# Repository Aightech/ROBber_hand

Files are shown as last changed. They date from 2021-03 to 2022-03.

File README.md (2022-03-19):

# Robotics ROBber Hand

## Description
ROBber hand is a robotic version of the rubber hand experiment. A webcam captures the position of the fingertips (with colour markers) and sends the angle to the device. The device is composed of four servo motors driven by a PCA9685 driver and an Arduino Uno. A fake hand is placed on top of the device and each finger is pushed up by the device.

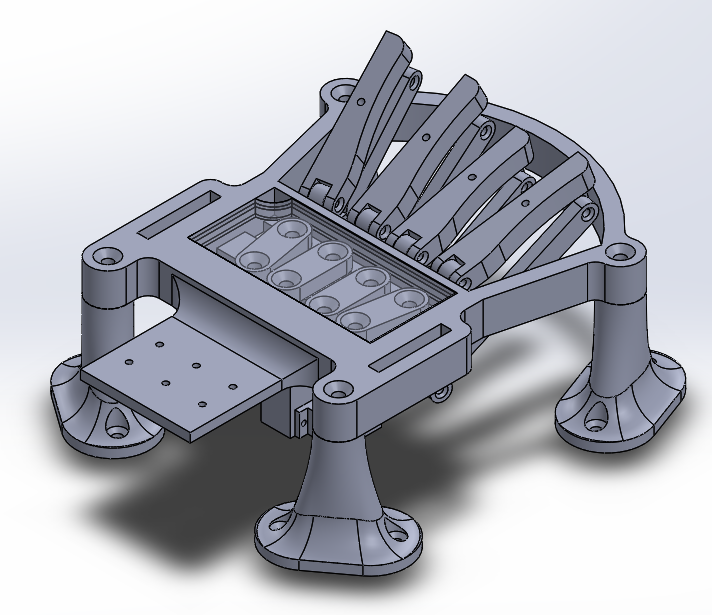
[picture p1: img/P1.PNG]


### List of material
- 4 servos motors MG90(metal gear) or SG90 (plastic gears)
- 1 servo driver PCA9685
- 1 arduino
- Screws and Bolts:
  - 8 M3-12mm
  - 4 M3-16mm
  - 12 M5-20mm
  - 4 M5 bolt

### Parts to print
- 1 frame
- 1 lid
- 4 foot
- 1 arduinoUNO and PCA holder
- 2 p1_short
- 2 p1_long
- 4 p2
- 2 p3_short
- 2 p3_long
- 2 p4_short
- 2 p4_long
- 4 bolt

## Requirements
- Python3/pip installed.

## Installation
### Electronics
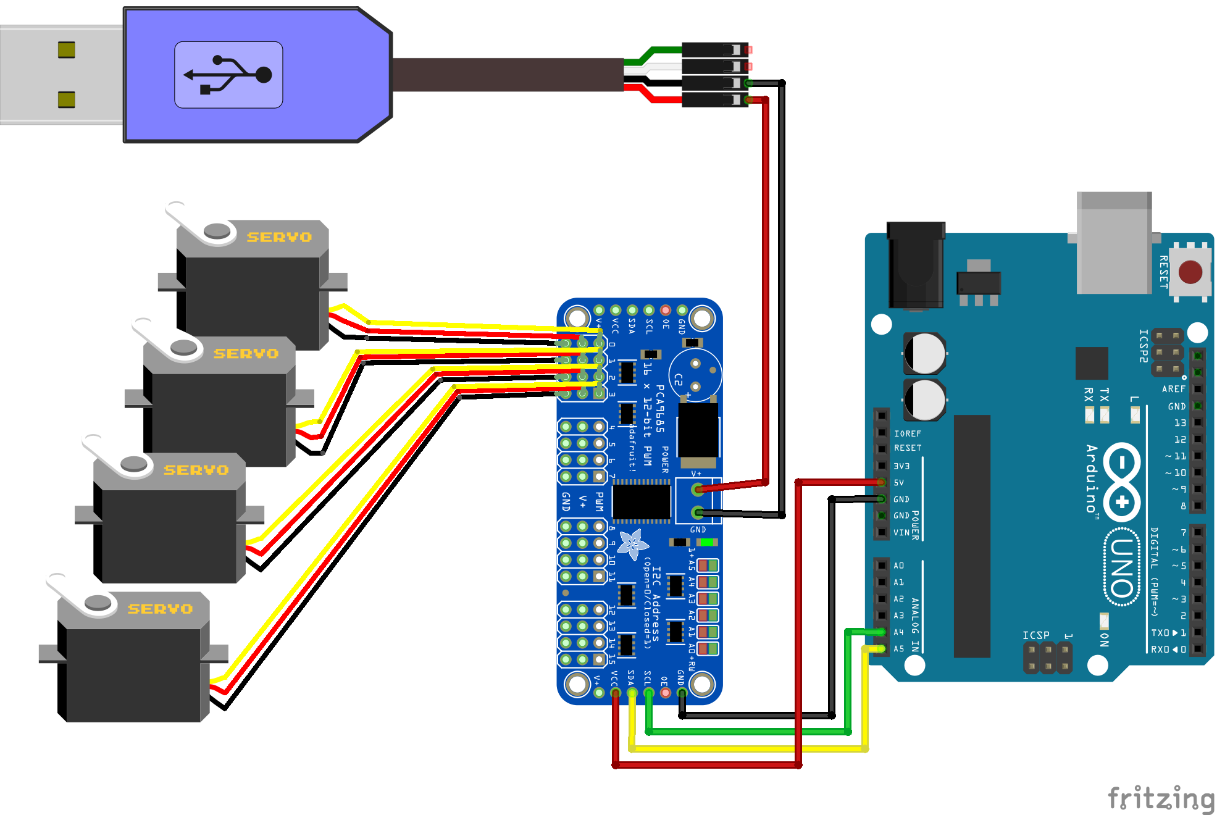
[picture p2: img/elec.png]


### Firmware
- Plug the arduino to the computer.
- Open the arduino IDE
- Ensure you have the last verdion of the library **Adafruit PWM Servo Driver** (go to the menu _sketch>Include library>Libraries Manager_ and search for "PWM".
- Open the file scripts/arduino.ide of the repository
- Upload it on the arduino board. 

### Software
- Download the zip folder at https://github.com/Aightech/ROBber_hand .
- Extract it
- Open the folder.
- Open the folder named **scripts**
- While pressing the **shift key** right click in the folder and select the option **open PowerShell**

Inside the PowerShell terminal:
- Install required libraries by entering the following command in the PowerShell terminal.
```bash 
pip install -r requirements.txt
```
## Usage

### Setup
- Plug the arduino USB wire to the computer.
- Plug the Webcam to the computer.
- Connect the motor driver to a power supply (ex: a phone charger).

### Setting:
To ensure the different parameters of the experiments are correct run the program setting with the command:
```bash 
python setting.py <NB_CAM> 
```
Replace :
- **<NB_CAM>** by the number of the webcam (usually 1 for laptop with integrated cam, else 0).

### Experiment
To launch the experiment use the command:
```bash 
python run.py <ARDUINO_PORT> <NB_CAM>
```
Replace :
- **<ARDUINO_PORT>** by the port used by the arduino (usually COM3, COM4, ...).
- **<NB_CAM>** by the number of the webcam (usually 1 for laptop with integrated cam, else 0).

### Options

in the script named **scripts/run.py** you can modify the following lines to modify the behavior of the robot.
```python
# BUFFER SIZE AND LOOKUP TABLE
lookup_table = [0, 1, 2, 3] # [nb finger cmd] => nb finger controlled
BUFF_SIZE = 1 # Delay of the control (no unit... depends of you communication speed)
inverted_finger = False  # When human finger up => robot finger down 
```

# Debug

In a terminal you can use the script **sendCmd.sh** to send position order to the Robber hand. Here an exemple:
```bash
Usage: scripts/sendCmd.sh [pos1] [pos2] [pos3] [pos4] port
Ex: scripts/sendCmd.sh 20 40 50 60 /dev/ttyUSB0
```

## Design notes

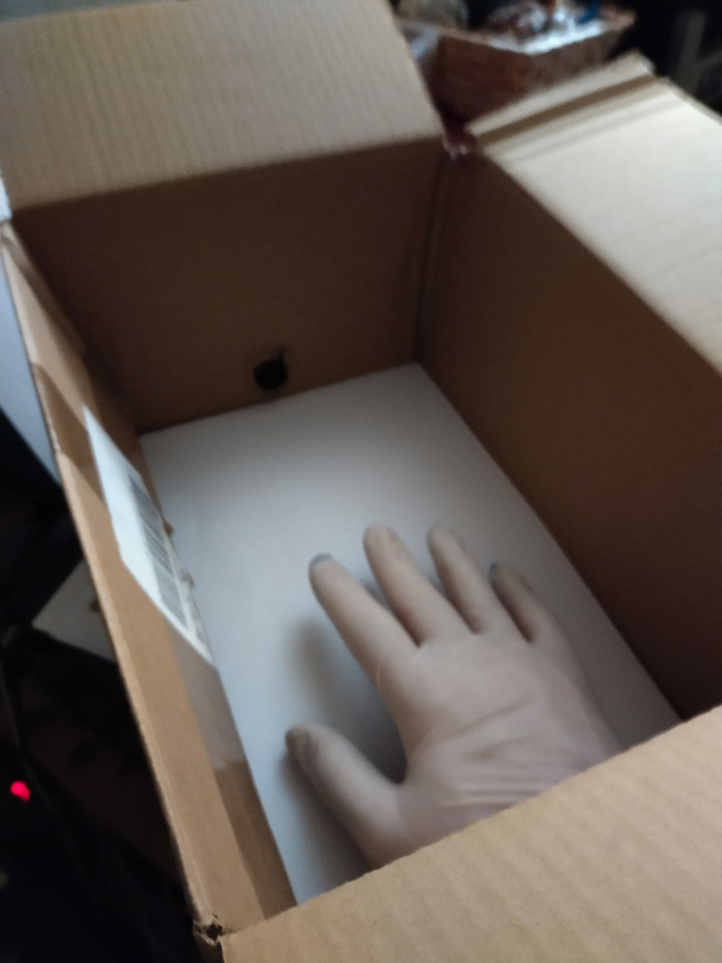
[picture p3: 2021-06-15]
img/SAVE_20210615_120732.jpg

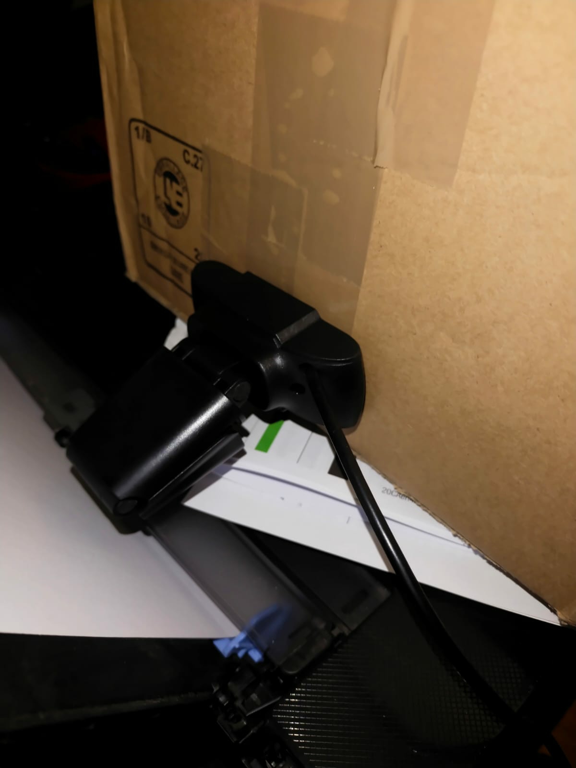
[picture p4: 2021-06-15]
img/SAVE_20210615_120804.jpg

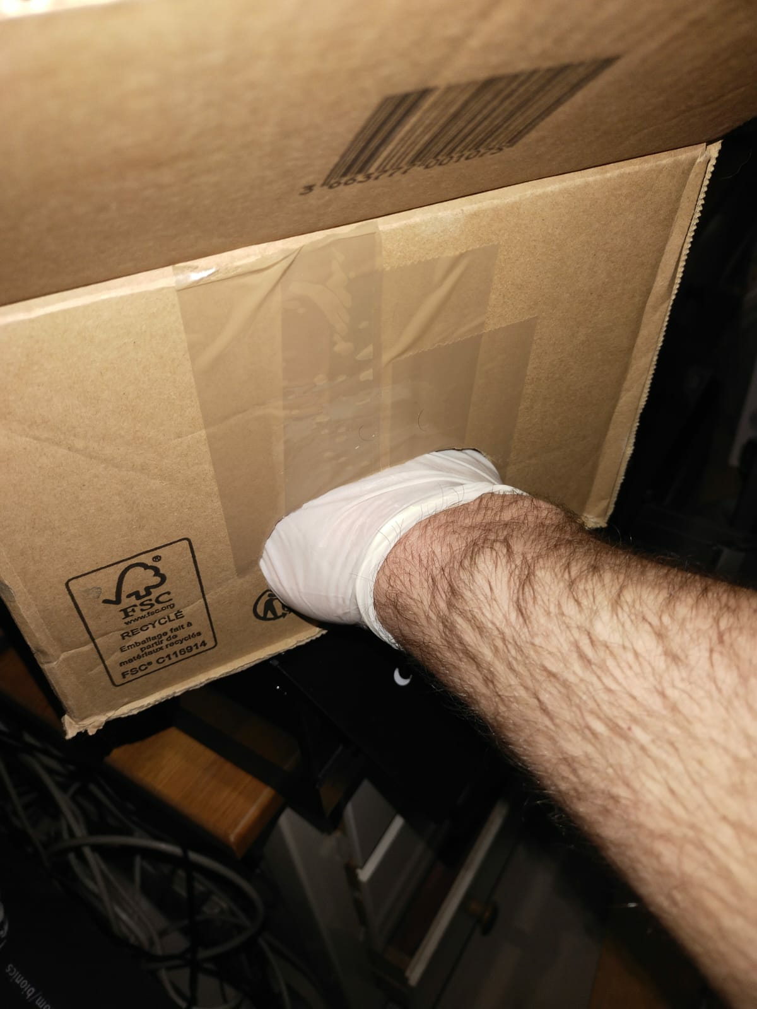
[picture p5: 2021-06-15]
img/SAVE_20210615_120755.jpg

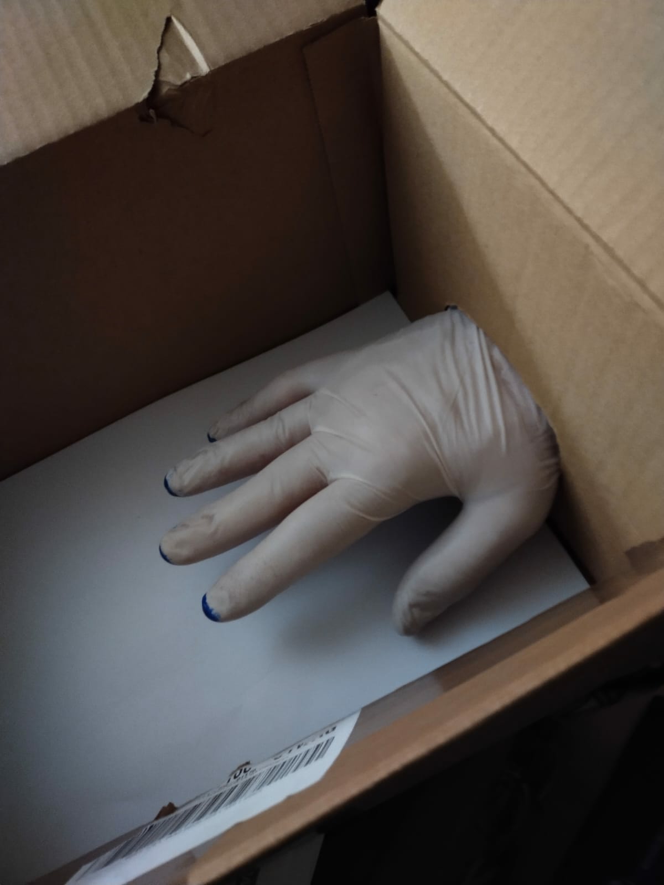
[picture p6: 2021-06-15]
img/SAVE_20210615_120743.jpg

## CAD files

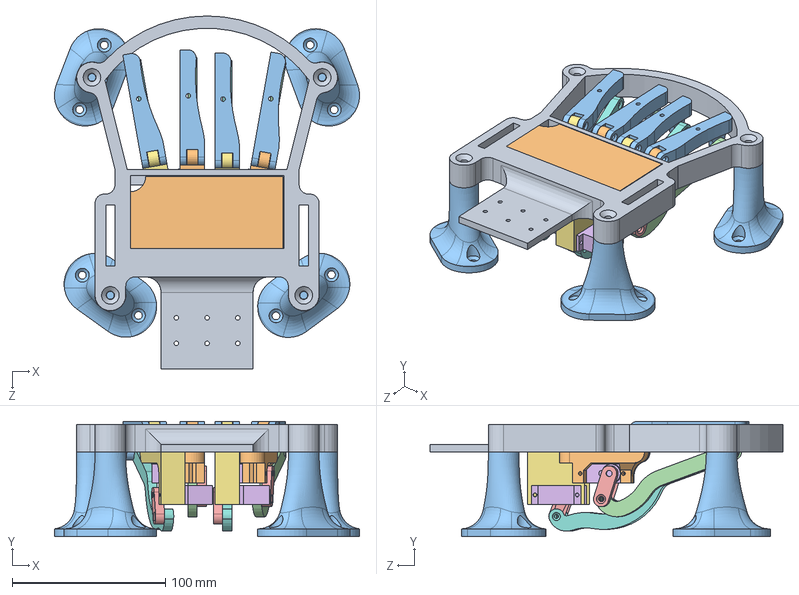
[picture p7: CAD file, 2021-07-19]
models/assemblage.SLDASM
198.7 x 75.0 x 230.0 mm
frame
p1_short x 2
p2 x 4
p3_short x 2
p4 x 4
sg90 x 4
p1_long x 2
p3_long x 2
bolt x 4
lid
foot x 4

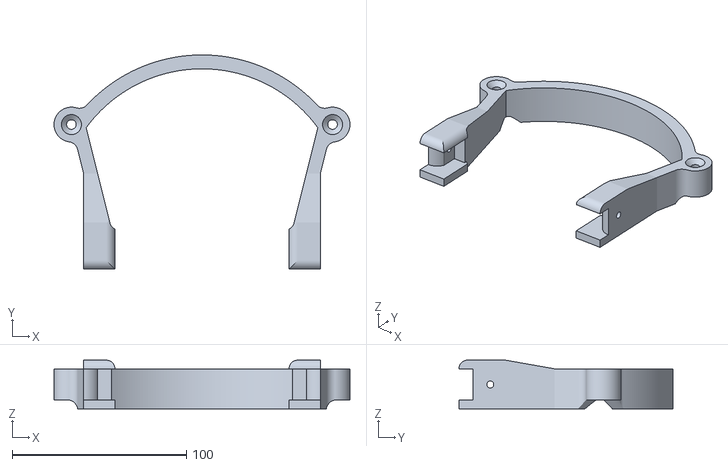
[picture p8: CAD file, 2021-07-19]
models/frame_v2-top.STL
170.0 x 123.0 x 28.0

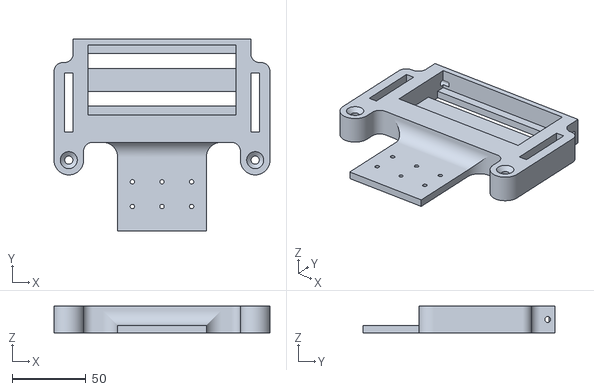
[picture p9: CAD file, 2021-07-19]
models/frame_v2-bottom.STL
146.0 x 130.0 x 18.0

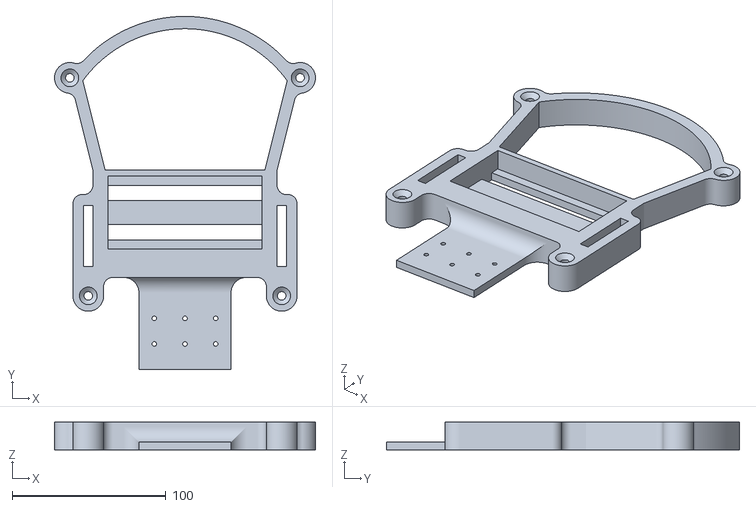
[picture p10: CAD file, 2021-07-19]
models/frame_Défaut.STL
170.0 x 230.0 x 18.0

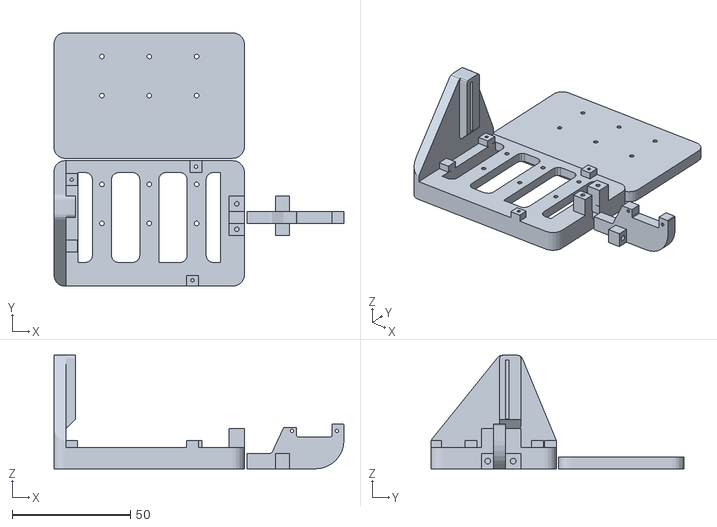
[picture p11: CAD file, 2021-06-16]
models/arduinoUNO_PCA_holder.stl
122.5 x 107.0 x 48.0

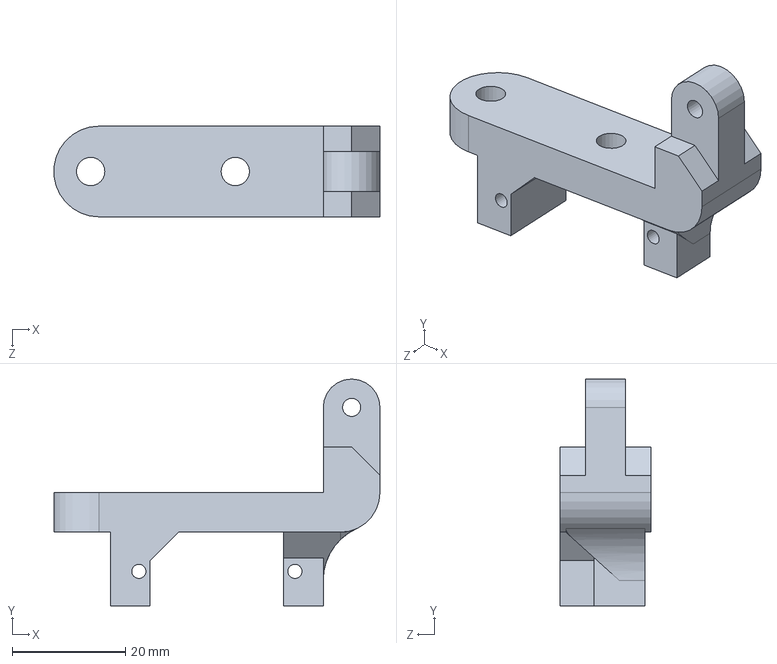
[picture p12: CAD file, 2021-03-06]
models/p1_short.SLDPRT
57.5 x 40.0 x 16.0 mm

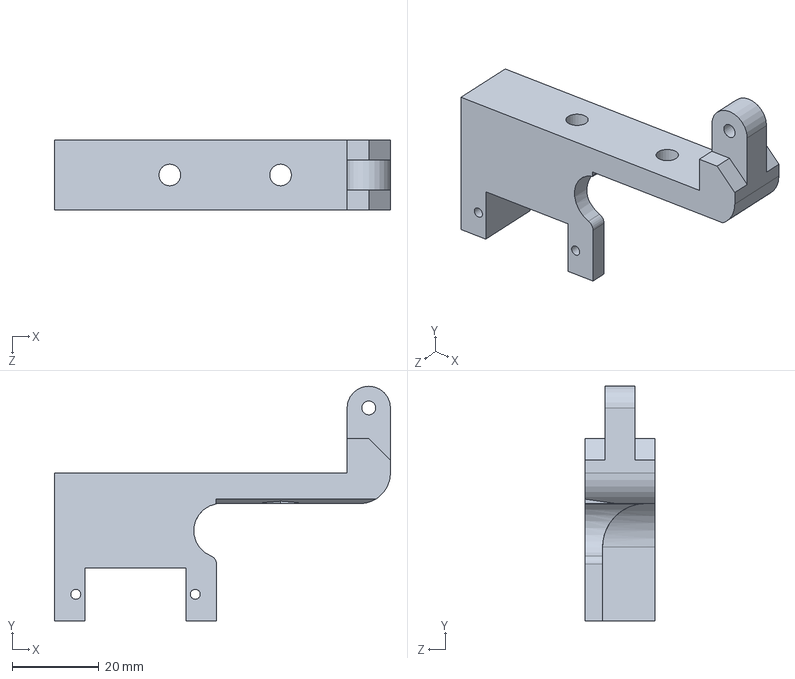
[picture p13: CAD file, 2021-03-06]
models/p1_long.SLDPRT
77.3 x 54.0 x 16.0 mm

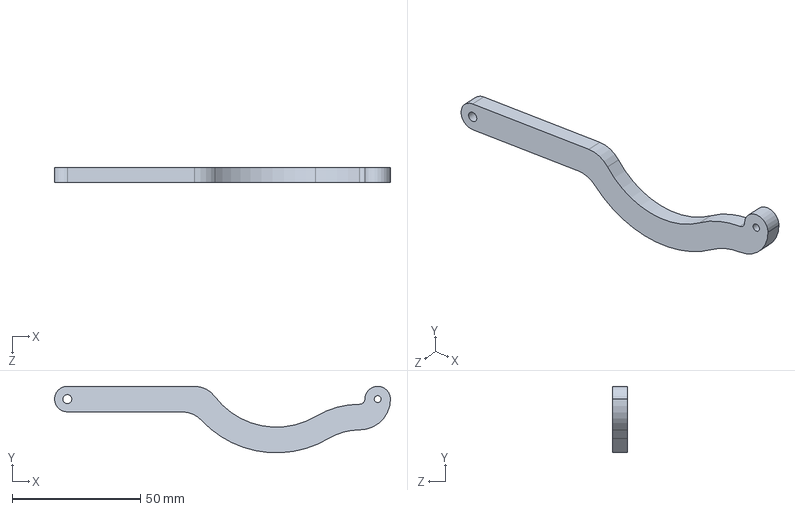
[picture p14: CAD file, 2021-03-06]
models/p3_long.SLDPRT
131.0 x 25.9 x 6.00 mm

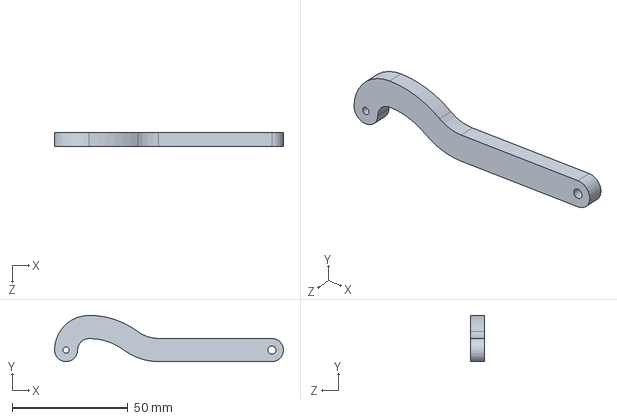
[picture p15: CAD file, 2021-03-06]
models/p3_short.SLDPRT
99.0 x 20.0 x 6.00 mm

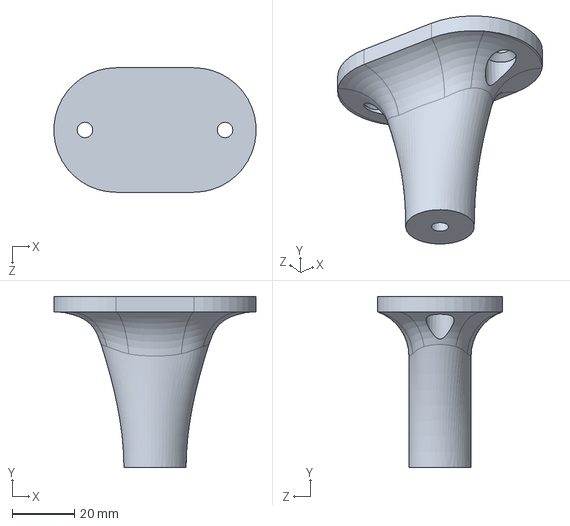
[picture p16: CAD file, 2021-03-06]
models/foot.SLDPRT
64.9 x 55.0 x 40.0 mm

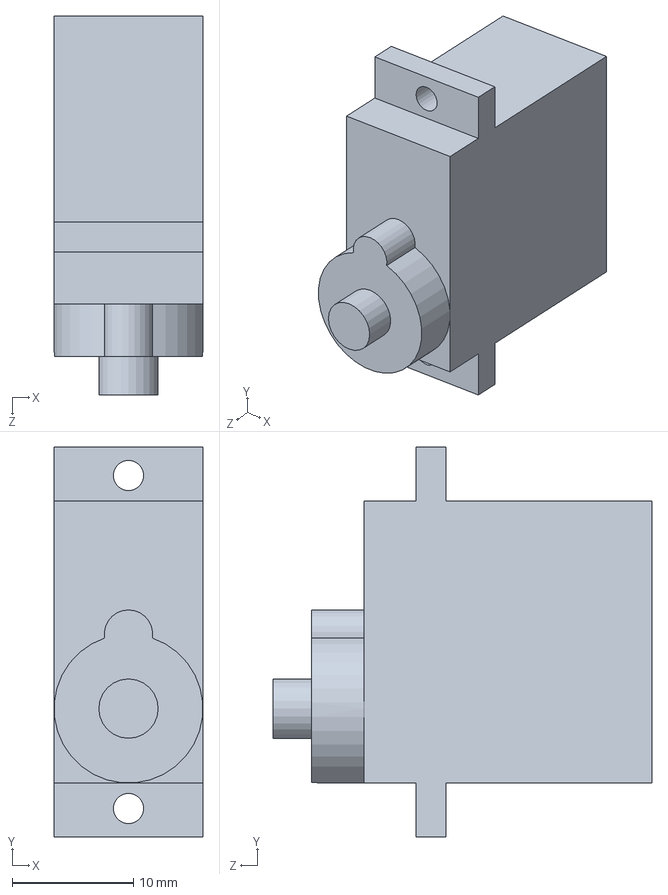
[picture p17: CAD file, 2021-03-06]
models/sg90.SLDPRT
12.3 x 32.2 x 31.3 mm

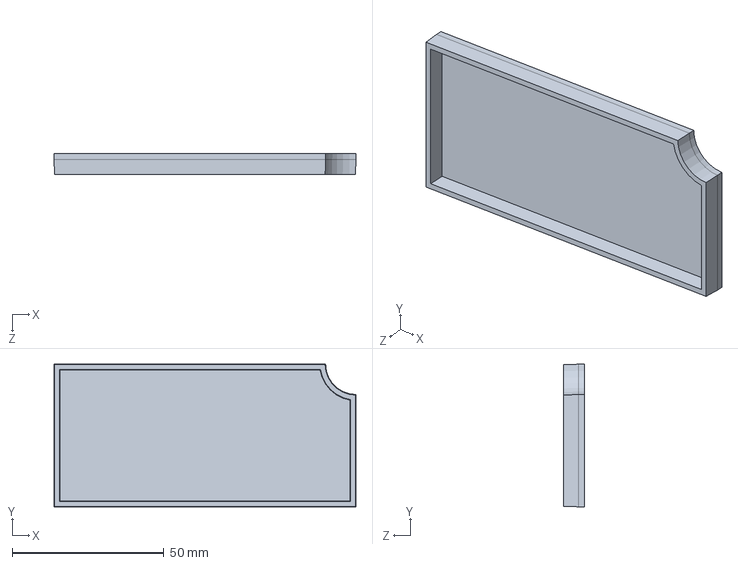
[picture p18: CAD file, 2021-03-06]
models/lid.SLDPRT
99.5 x 47.0 x 7.00 mm

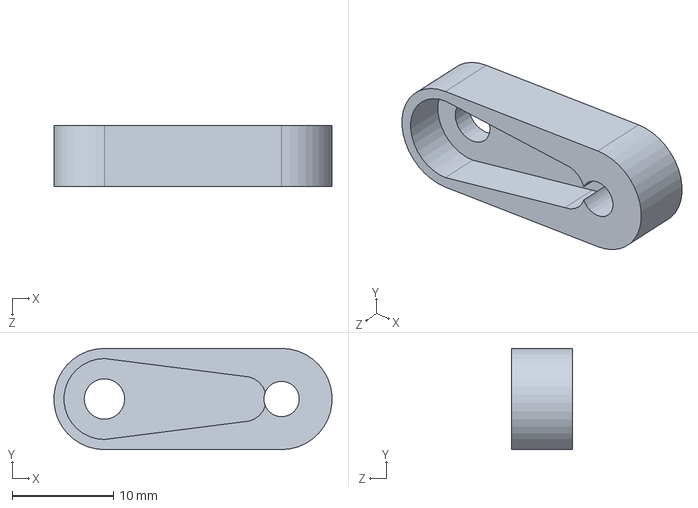
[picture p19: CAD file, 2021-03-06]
models/p4.SLDPRT
27.5 x 10.0 x 6.00 mm

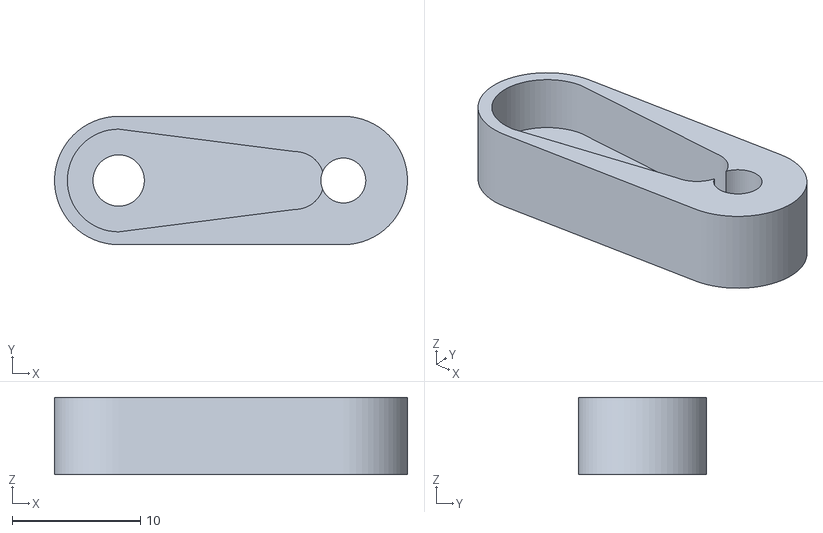
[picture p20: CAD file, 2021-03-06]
models/p4_short.STL
27.5 x 10.0 x 6.00

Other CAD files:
models/frame.SLDPRT
models/p4_long.STL
models/p2.SLDPRT
models/bolt.SLDPRT
models/assemblage.STL
models/bolt.STL
models/foot.STL
models/frame.STL
models/lid.STL
models/p1_long.STL
models/p1_short.STL
models/p2.STL
models/p3_long.STL
models/p3_short.STL

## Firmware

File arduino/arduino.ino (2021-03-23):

#include <Wire.h>
#include <Adafruit_PWMServoDriver.h>

Adafruit_PWMServoDriver pwm = Adafruit_PWMServoDriver();

//#define DEBUG
#define NB_FINGER 4
#define SERVOMIN  440 // This is the 'minimum' pulse length count (out of 4096)
#define SERVOMAX  470 // This is the 'maximum' pulse length count (out of 4096)
int s_range = SERVOMAX-SERVOMIN;

unsigned char crc;
unsigned char pos[NB_FINGER] = {20, 00, 100, 00};
int limit[NB_FINGER][2] = { {400, 280},
                                      {200, 385},
                                      {320, 170},
                                      {180, 360}};

void setup() {
  Serial.begin(9600);
  pinMode(13, OUTPUT);

  pwm.begin();
  pwm.setOscillatorFrequency(27000000);
  pwm.setPWMFreq(50);  // This is the maximum PWM frequency

   
}

void loop() {

 #ifdef DEBUG
//    for(int i =0; i<NB_FINGER; i++)
//         pwm.setPWM(i, 0, pos[i]/255.0f*(limit[i][1]-limit[i][0])+limit[i][0]);
    delay(15);
    int i = 3;
    pwm.setPWM(i, 0, 200);
  #endif
   
  
  while (Serial.available() > NB_FINGER+3)//wait for data
  {
    if(Serial.read()=='#' && Serial.read()=='#')//if the two first bytes are ## then decode
    {
      crc=0;
      for(int i =0; i<NB_FINGER; i++)//read data and compute crc
        crc += pos[i] = Serial.read();

      for(int i =0; i<NB_FINGER; i++)//read data and compute crc
        pos[i] = min(255, max(0, pos[i]));

      if( crc == Serial.read())//if crc is correct then set the servo position
      {
        for(int i =0; i<NB_FINGER; i++)
          pwm.setPWM(i, 0, pos[i]/255.0f*(limit[i][1]-limit[i][0])+limit[i][0]);
        Serial.write(1);//return the crc
      }
      else
        Serial.write(0);
         
      delay(15);
    }
  }
}
